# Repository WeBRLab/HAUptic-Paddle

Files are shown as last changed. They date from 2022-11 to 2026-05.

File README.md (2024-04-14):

# Haptic Paddle
<h2> This repository contains the design files and software for a single-DOF haptic display for STEM education.</h1>

<br/><br/><br/>
By: Auburn University Wearable and Bio-Robotics Lab <br/>
PI: **Chad G. Rose**  <br/>
Graduate Researchers: **Chandler Stubbs**, **Rhet Hailey**, **Avinash Baskaran**  <br/>
Undergraduate Researchers: **Zack Miller**, **Jamison Hood** <br/>

Instructions for flashing new code in Python:

1. Follow this tutorial to install micropython and configure micropython interpretter on logic board:
https://docs.sunfounder.com/projects/thales-kit/en/latest/micropython/python_start/install_micropython_to_pico.html

2. Run or Save your code on the RPI logic board as "main.py"

3. (optional) eject and re-insert USB cable to start code automatically.

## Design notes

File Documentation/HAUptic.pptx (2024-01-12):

## HAUptic Paddle

Avinash Baskaran
Chad G. Rose

## Hardware: Commercial Components

## Hardware: 3D Printing

## Electronics: PCB

## Electronics: PCB internal connections

GND
DNC
DNC
DNC
HIGH
Dir (1/0)
Dir (1/0)
PWM

….

GND
Motor (+)
Motor (-)
DNC
DNC
GND
Supply (5v) +
Supply (12v) +

…

DNC

## Electronics: PCB external connections

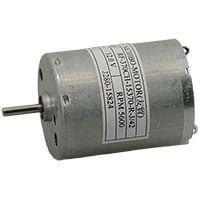
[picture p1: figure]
RF370CH-15370-R

DNC

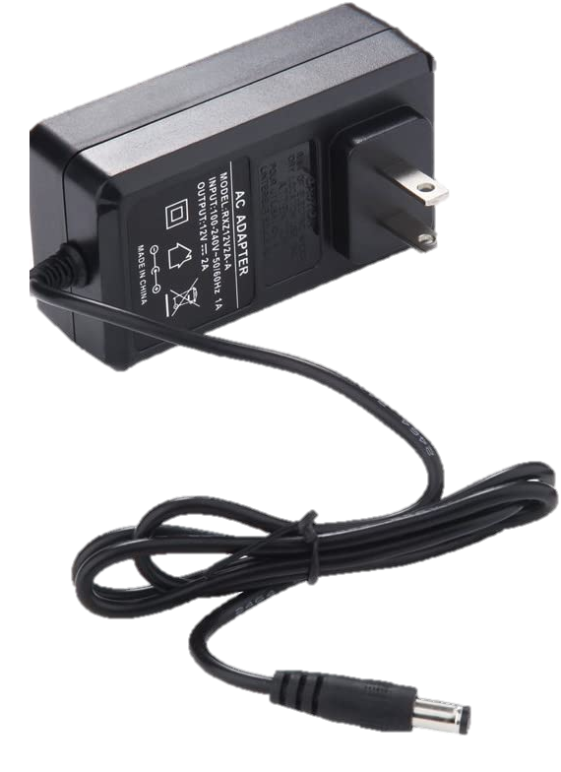
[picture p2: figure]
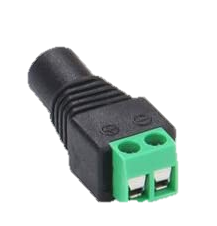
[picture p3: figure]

## Electronics: PCB external connections

DNC

## Software: Interfacing

## Assembly

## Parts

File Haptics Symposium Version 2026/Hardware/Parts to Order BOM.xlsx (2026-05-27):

Item | Cost Per Pack | No. Per Pack | No. Per Paddle | Cost Per Paddle | Vendor | Link | Column1
PLA (~.2 kg/paddle) | $28.00 | 1 | 0.2 | $5.60 | Amazon | https://www.amazon.com/HATCHBOX-Printer-Filament-Dimensional-Accuracy/dp/B09G8HDL1Q
Xiao Seeed ESP32S3 | $7.49 | 1 | 1 | $7.49 | Digikey | https://www.digikey.com/en/products/detail/seeed-technology-co-ltd/113991114/19285530?gclsrc=aw.ds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 | **Version Used for Evaluating Usability Between Low Cost and High End Haptic Paddles (Haptics Symposium 2026)
Xiao Boards (RP2040) | $6.50 | 1 | 1 | $6.50 | Mouser | https://www.mouser.com/ProductDetail/Seeed-Studio/102010388?qs=hd1VzrDQEGhCsl7tLa3o%252Bg%3D%3D&mgh=1 | **Version Used for Work-in-Progress Interface and Design Upgrades to Design Paper (Haptics Symposium 2026)
5V Voltage Regulator (Pololu 0J8557) | $8.95 | 1 | 1 | $8.95 | Pololu | Pololu 5V, 500mA Step-Down Voltage Regulator D24V5F5 (https://www.pololu.com/product/2843)
Motor Drivers | $14.50 | 1 | 1 | $14.50 | Sparkfun | https://www.sparkfun.com/sparkfun-motor-driver-dual-tb6612fng-with-headers.html
Cables | $15.00 | 33 | 1 | $0.45 | Amazon | https://www.amazon.com/Gauge-Wire-Solid-Hookup-Wires/dp/B088KQFHV7
Motors | $4.95 | 1 | 1 | $4.95 | Jameco | https://www.jameco.com/z/RF370CH-15370-R-Nichibo-Taiwan-12V-DC-Motor-5600-RPM-2mm-Round-Shaft_2327887.html
Bearings/bushings | $0.92 | 1 | 1 | $0.92 | McMaster | https://www.mcmaster.com/2938T3/
Shoulder bolt | $6.88 | 1 | 1 | $6.88 | McMaster | https://www.mcmaster.com/90311A144/
Neoprene Tubing | $1.27 | 1 | 0.08333333333 | $0.11 | McMaster | https://www.mcmaster.com/51075K27/
Solder | $7.39 | 50 | 5 | $0.74 | Amazon | https://www.amazon.com/TOWOT-Electrical-Soldering-Content-Sn60-Pd40/dp/B0943TPRXK
Heat shrink | $9.00 | 32.81 | 0.5 | $0.14 | Amazon | https://www.amazon.com/Othmro-Pieces-Heat-Shrinking-Ratio/dp/B07W4NZSSN
Magnets | $3.93 | 1 | 1 | $3.93 | McMaster | https://www.mcmaster.com/57295K73/
Sensor | $6.65 | 1 | 1 | $6.65 | Digikey | SS49E Honeywell Sensing and Productivity Solutions | Linear, Compass (ICs) | DigiKey (https://www.digikey.com.au/en/products/detail/honeywell-sensing-and-productivity-solutions/SS49E/701361)
Female header connector | $9.99 | 60 | 0.125 | $0.02 | Amazon | https://www.amazon.com/Qunqi-2-54mm-Straight-Connector-Arduino/dp/B07CGGSDWF
10-24 Steel Hex Nut | $2.33 | 100 | 1 | $0.02 | McMaster | https://www.mcmaster.com/90480A011/
8-32 Steel Hex Nut | $2.02 | 100 | 4 | $0.08 | McMaster | https://www.mcmaster.com/90480A009/
10-44 Steel Hex Nut | $2.33 | 100 | 1 | $0.02 | McMaster | https://www.mcmaster.com/90480A011/
PCB | Contact ___mdm0115@auburn.edu____ |  |  | $2.33
 |  |  | Price Per Paddle | $62.79 | Without WiFI
 |  |  |  | $63.78 | With WiFi
If Desired/Needed for Connection
Rubber Feet | $24.94 | 10 | 4 | $9.98 | McMaster | https://www.mcmaster.com/53535A22/ |  | Useful for a sturdy connection to test surface
Power supplies | $13.99 | 2 | 1 | $7.00 | Amazon | https://www.amazon.com/ALITOVE-Converter-100-240V-Transformer-Security/dp/B082C6XF88?hvadid=694095447987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 |  | Useful if desired to plug into a wall outlet
USB cable | $13.00 | 2 | 1 | $6.50 | Amazon | https://www.amazon.com/Upgrade-CONMDEX-Android-Charging-Transfer/dp/B087JMJSVC |  | Necessary if lacking a USB/USB-C Cable

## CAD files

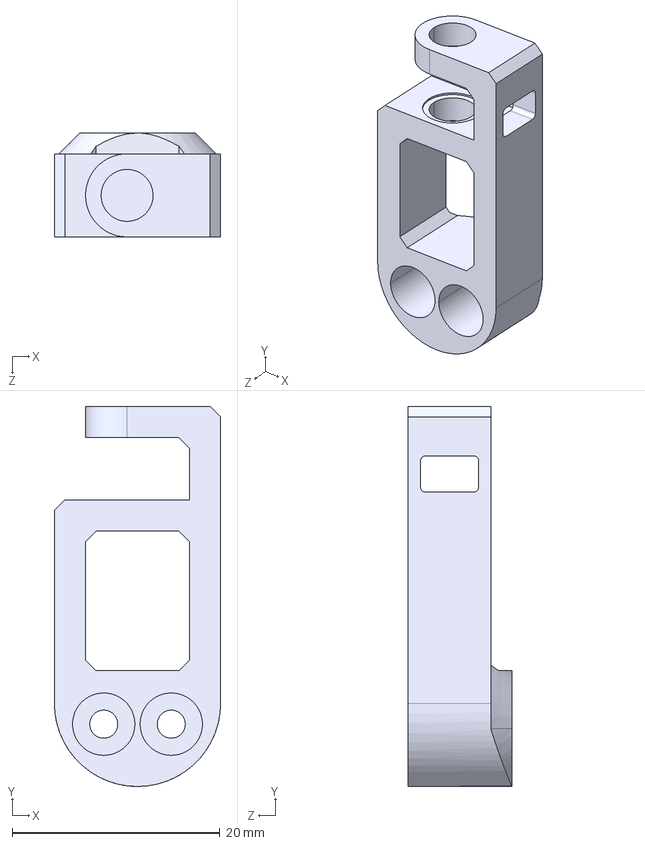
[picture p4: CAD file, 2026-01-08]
Haptics Symposium Version 2026/Hardware/STEP Files/Magnet Holder.STEP
16.0 x 36.6 x 10.0 mm

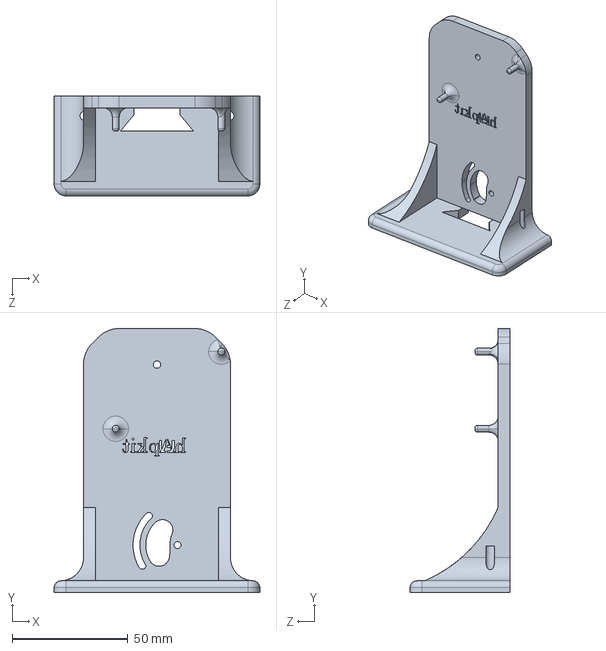
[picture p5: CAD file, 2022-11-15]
Hardware/step/Base_A-1.STEP
88.9 x 114.1 x 43.2 mm

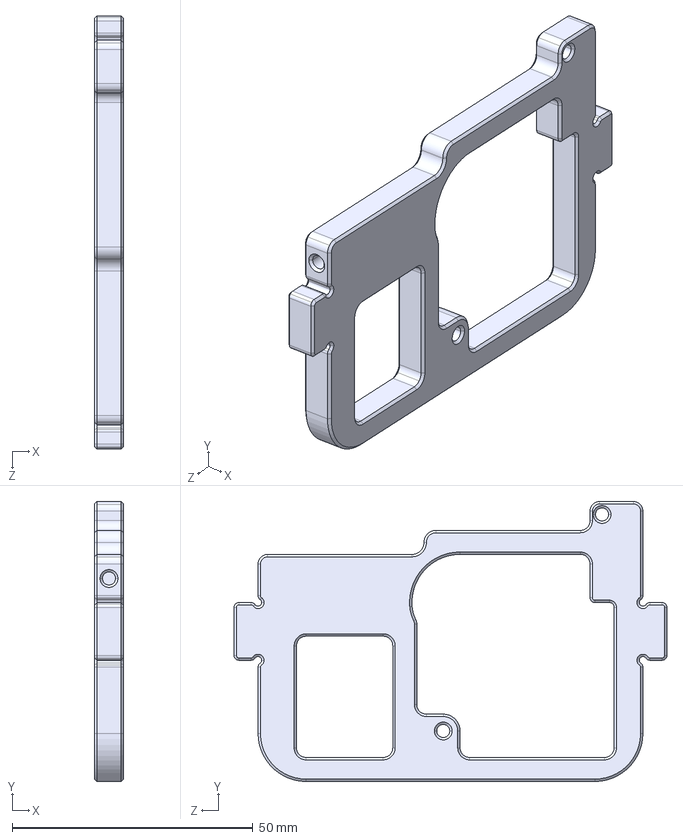
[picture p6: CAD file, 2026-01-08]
Haptics Symposium Version 2026/Hardware/STEP Files/Paddle - PCB Plate.STEP
6.00 x 58.2 x 90.0 mm

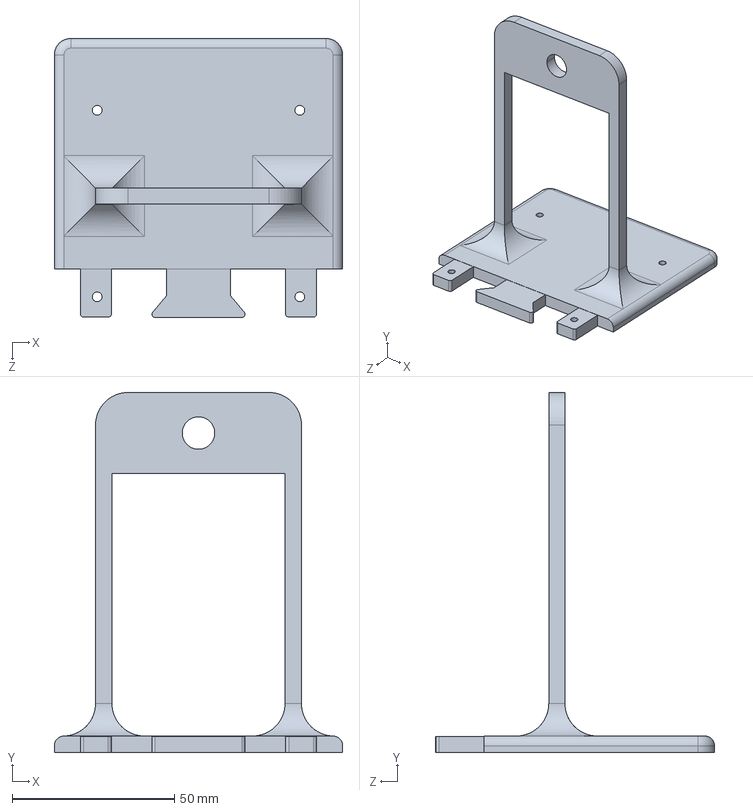
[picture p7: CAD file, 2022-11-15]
Hardware/step/Base_B-1.STEP
88.9 x 111.0 x 86.1 mm

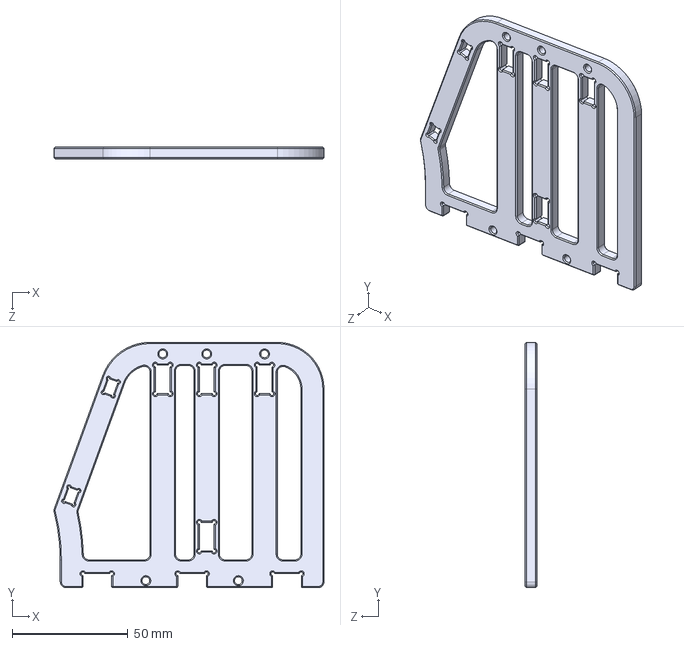
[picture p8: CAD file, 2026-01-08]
Haptics Symposium Version 2026/Hardware/STEP Files/Paddle - Side Plate.STEP
116.7 x 106.0 x 5.00 mm

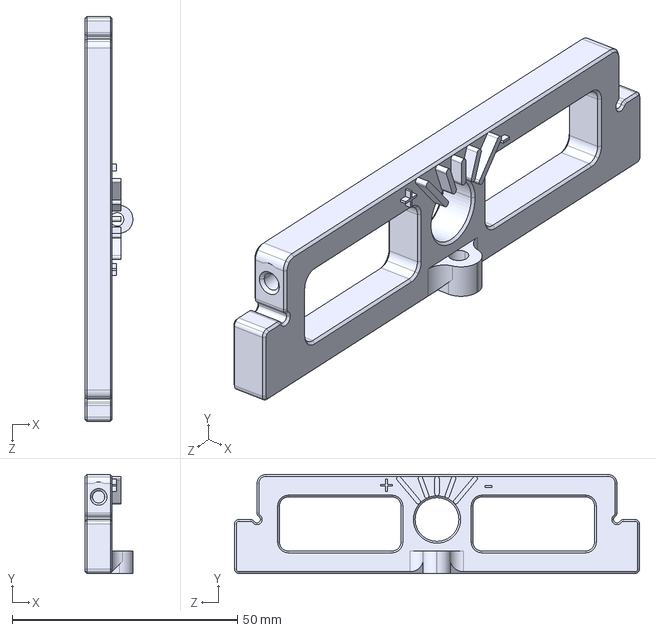
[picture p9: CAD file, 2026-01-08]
Haptics Symposium Version 2026/Hardware/STEP Files/Front Calibration Support Plate.STEP
10.6 x 22.0 x 90.0 mm

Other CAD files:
Haptics Symposium Version 2026/Hardware/Solidworks Files/Assembly/HapKit Assembly.SLDASM
Hardware/HAUPTIC_PADDLE.SLDASM
Hardware/CAD/tb6612fng.step.SLDASM
Hardware/CAD/Assembly.SLDASM
Hardware/CAD/capacitor.step.SLDPRT
Hardware/CAD_files/Sector_Pulley - adjusted.SLDPRT
Hardware/Base_B.SLDPRT
Hardware/CAD/Motor_Paddle_Interface.step.SLDPRT
Hardware/CAD_files/Base.1.SLDPRT
Hardware/Base_A.SLDPRT
Hardware/CAD/header_8.step.SLDPRT
Hardware/CAD_files/Sector_Pulley_1.SLDPRT
Haptics Symposium Version 2026/Hardware/STEP Files/Mini Plate with Nut.STEP
Haptics Symposium Version 2026/Hardware/STEP Files/Motor_Pulley.STEP
Haptics Symposium Version 2026/Hardware/STEP Files/Paddle - Bottom Plate.STEP
Haptics Symposium Version 2026/Hardware/STEP Files/Paddle - PCB Side Plate.STEP
Haptics Symposium Version 2026/Hardware/STEP Files/Paddle - Washer.STEP
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

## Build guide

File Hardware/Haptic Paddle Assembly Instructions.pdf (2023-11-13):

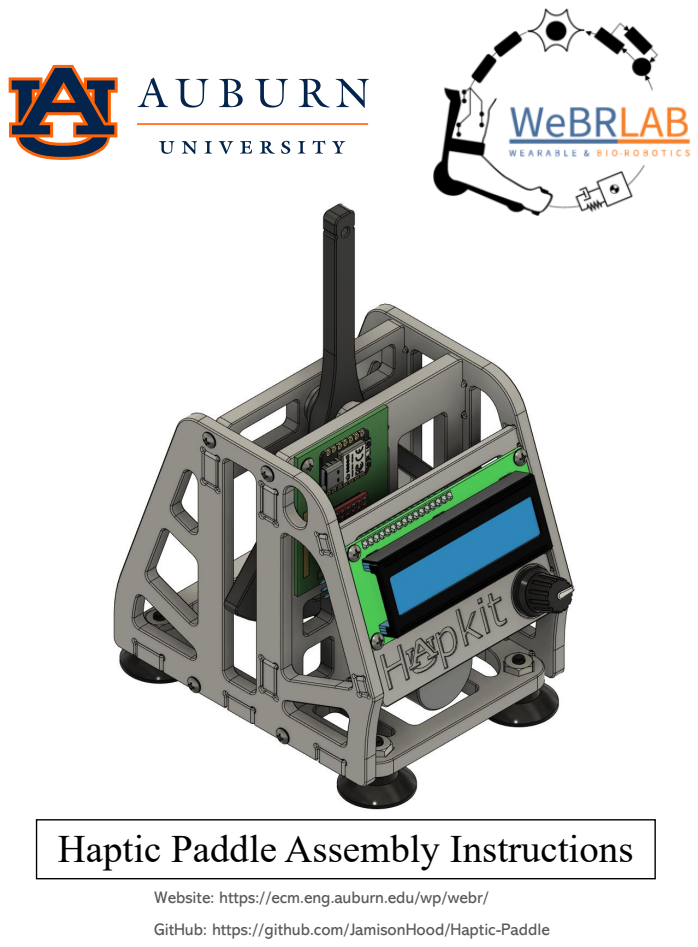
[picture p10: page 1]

Haptic Paddle Assembly Instructions

Website: https://ecm.eng.auburn.edu/wp/webr/

GitHub: https://github.com/JamisonHood/Haptic-Paddle

P a g e | 2

## Table of Contents

## Required Components

## Electronics

Part Name | Quantity | Image
Rotary Encoder | 1

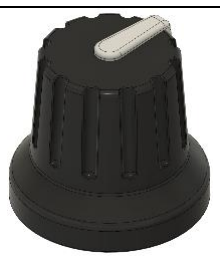
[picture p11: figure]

Encoder Knob | 1
Control Board | 1
Brushed Motor | 1

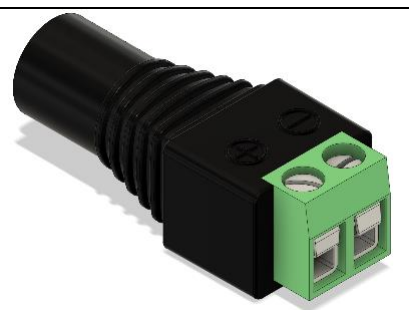
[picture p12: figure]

Barrel Power Connector | 1

LCD Display | 1

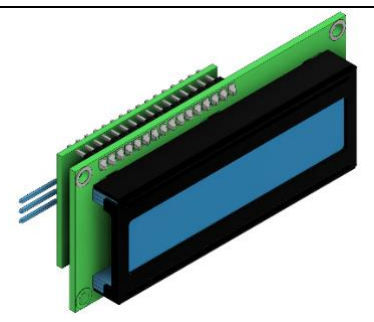
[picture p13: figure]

## Hardware

Part Name | Quantity | Image
¼ Inch Shoulder Bolt | 1
¼ Inch Sleeve Bushing | 1

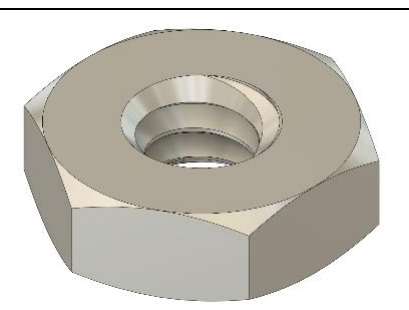
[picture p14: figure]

10-24 Nut (For Shoulder Bolt) | 1
Rubber Feet | 4

8-32 Nut (For Rubber Feet) | 4

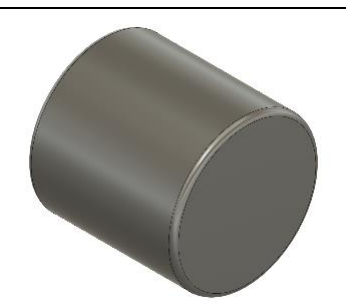
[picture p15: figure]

Disc Magnet | 1

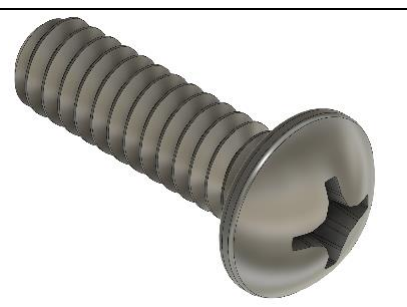
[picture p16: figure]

18-8 Pan Head Screw | 16

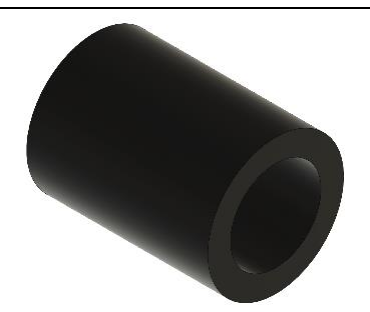
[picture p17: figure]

Rubber Sleeve | 1

## 3D printed Components

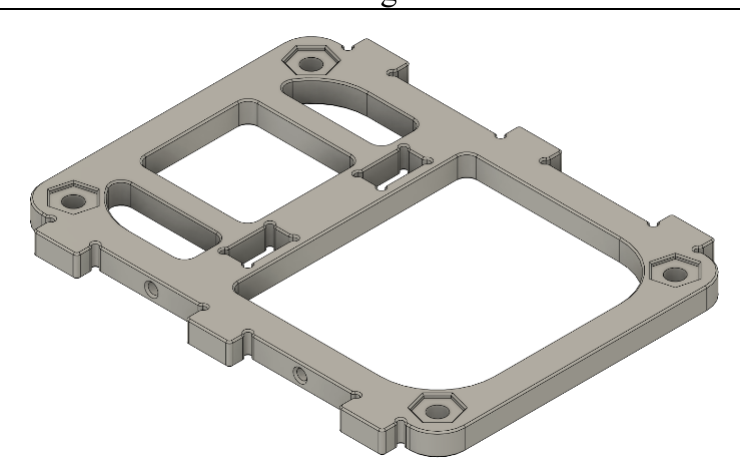
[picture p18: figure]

Part Name | Quantity | Image
Base Plate | 1
Motor and Electronics Plate | 1
LCD Frame | 1

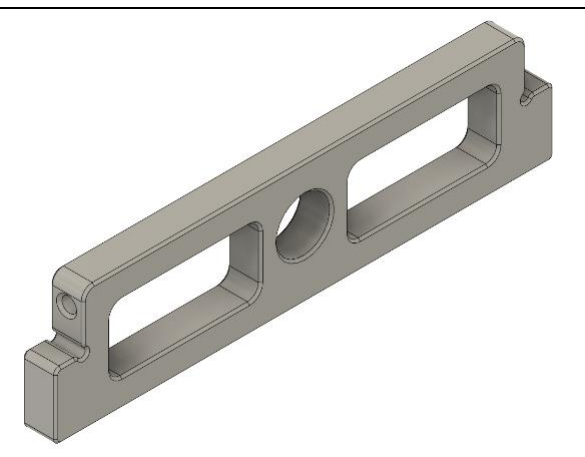
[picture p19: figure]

Shoulder Support Plate | 1

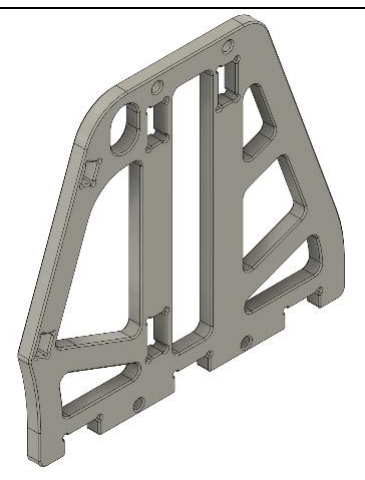
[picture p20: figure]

Left Side Plate | 1
Right Side Plate | 1

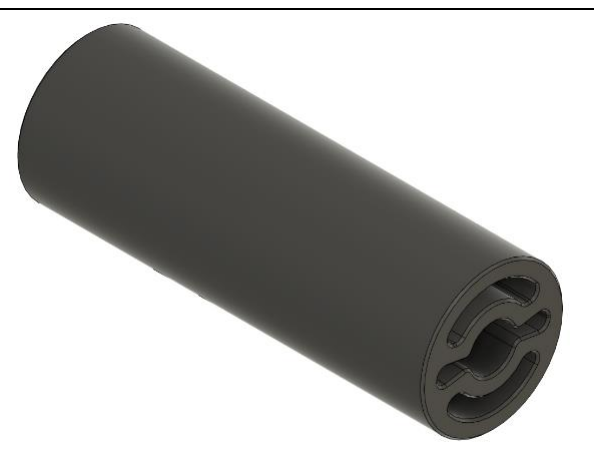
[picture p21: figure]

Motor Pulley | 1

P a g e |

8

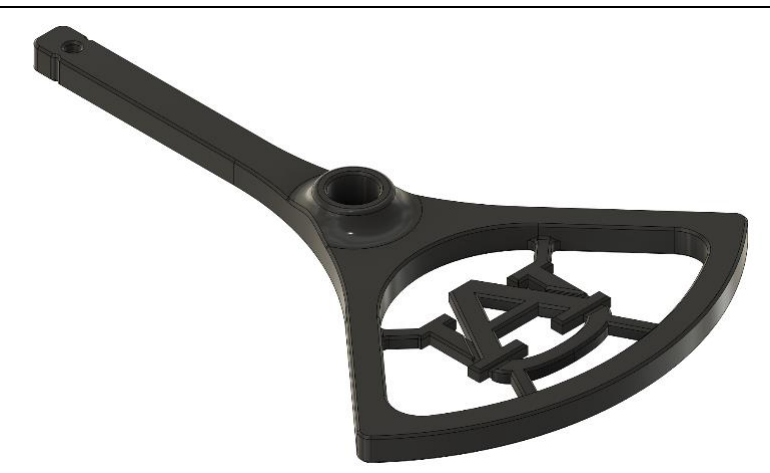
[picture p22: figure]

Paddle
1

1 | Assembly Steps

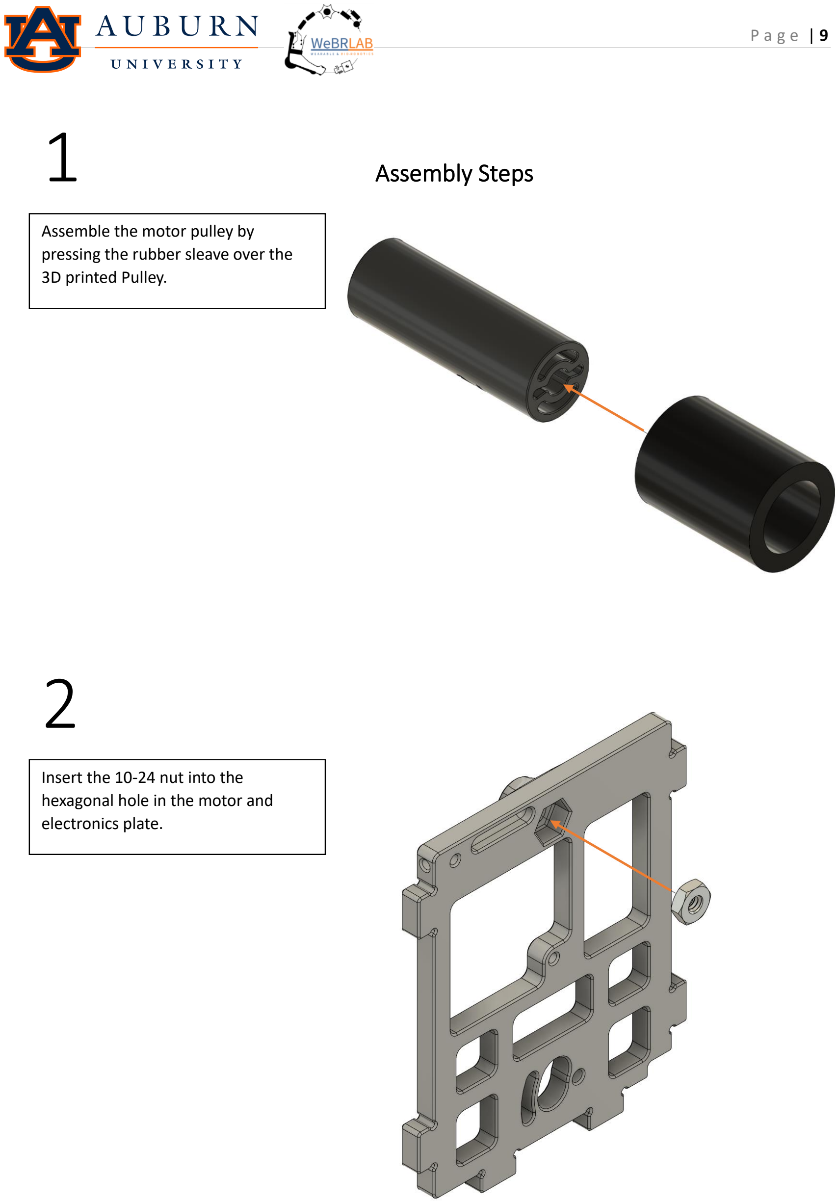
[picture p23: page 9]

2

Assemble the motor pulley by pressing the rubber sleave over the 3D printed Pulley.

Insert the 10-24 nut into the hexagonal hole in the motor and electronics plate.

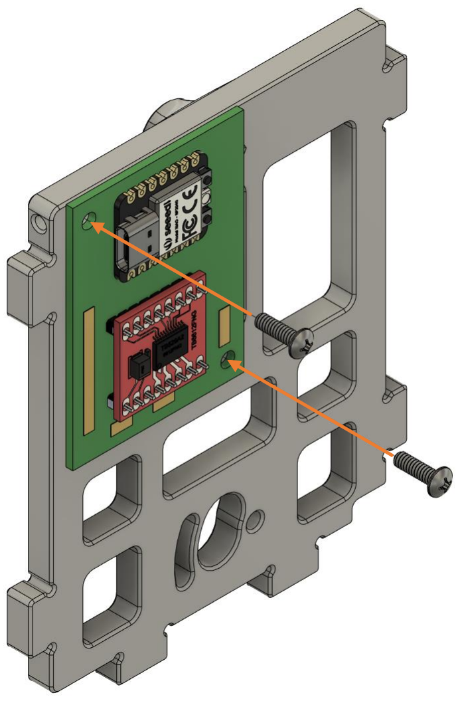
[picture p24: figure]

3

4

Attach the electronics PCB using 2 #18-8 Screws.

Note: Make sure the #10-24 nut is in place as it will not be accessible after this step.

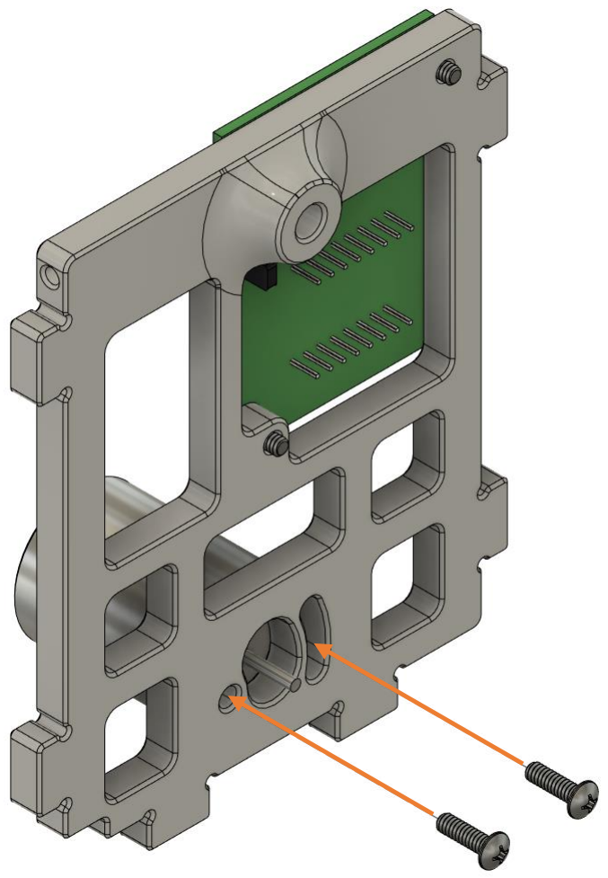
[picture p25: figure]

Attach the brushed motor using 2 #18-8 screws. Leave the screws loose such that the motor can freely swing in its mount.

5

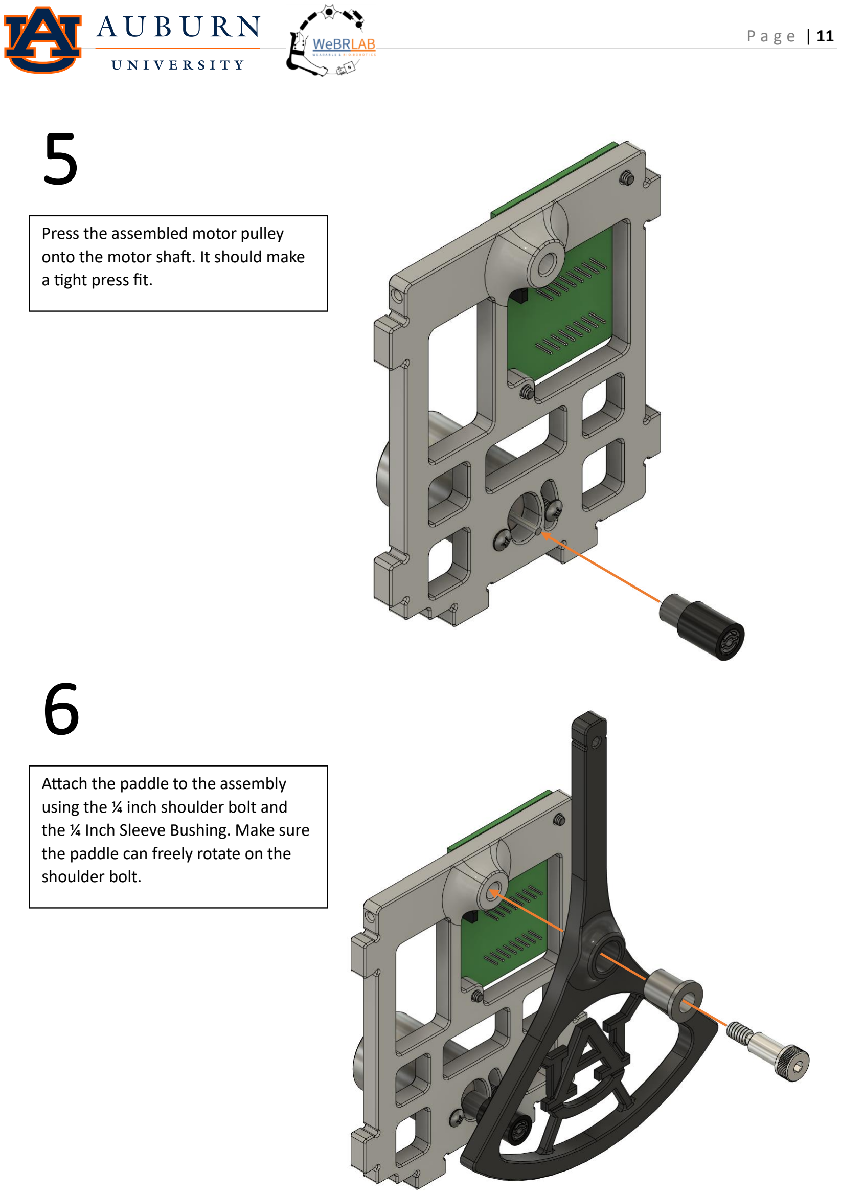
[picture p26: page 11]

6

Press the assembled motor pulley onto the motor shaft. It should make a tight press fit.

Attach the paddle to the assembly using the ¼ inch shoulder bolt and the ¼ Inch Sleeve Bushing. Make sure the paddle can freely rotate on the shoulder bolt.

7

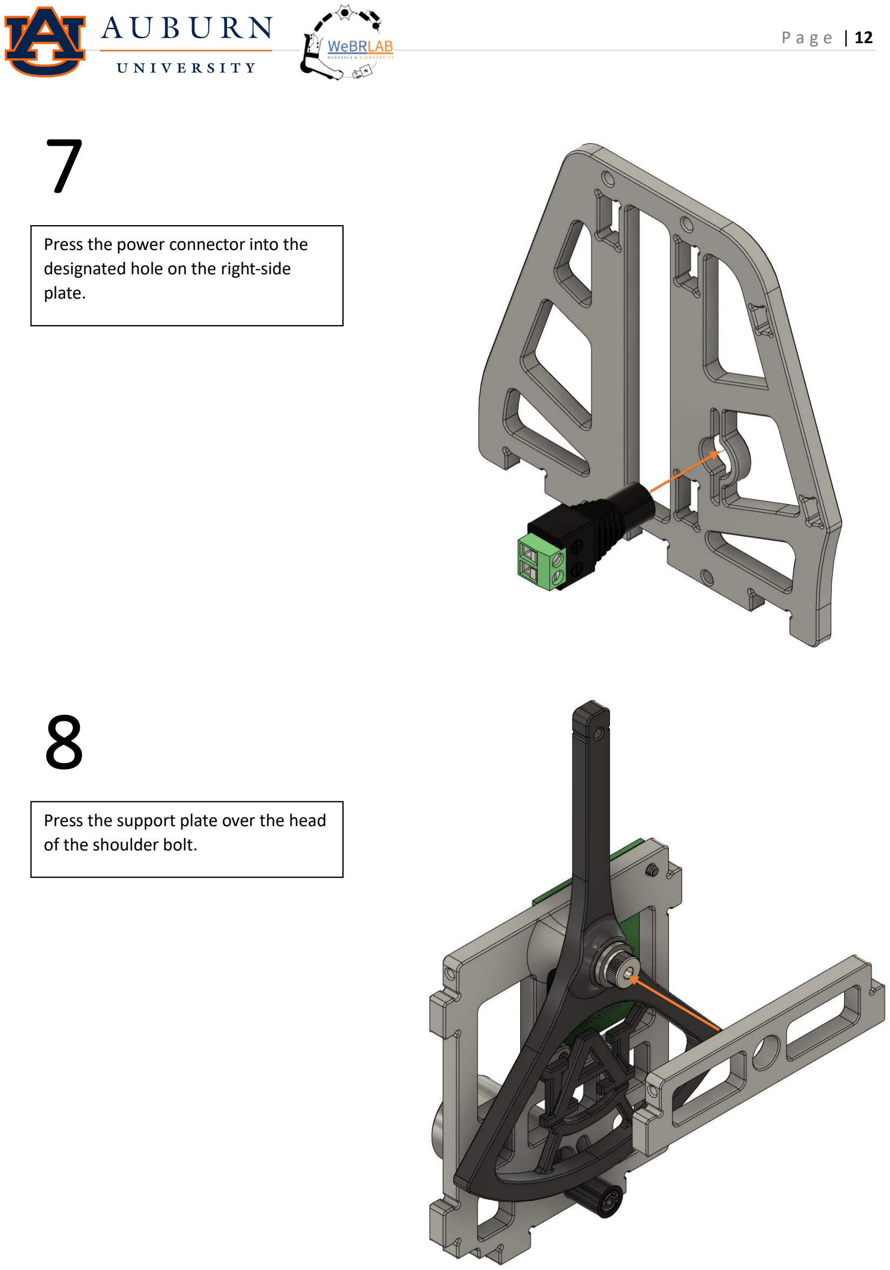
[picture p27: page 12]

8

Press the power connector into the designated hole on the right-side plate.

Press the support plate over the head of the shoulder bolt.

9

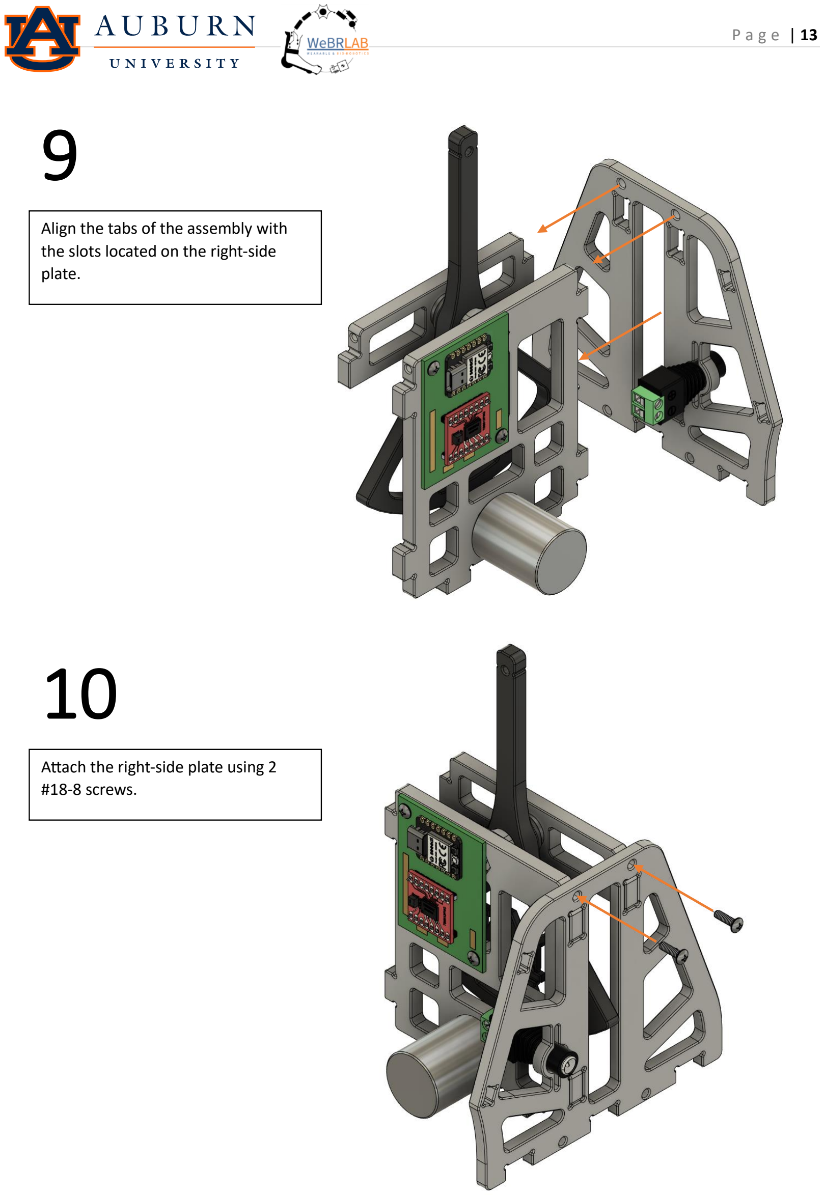
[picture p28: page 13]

10

Align the tabs of the assembly with the slots located on the right-side plate.

Attach the right-side plate using 2 #18-8 screws.

11

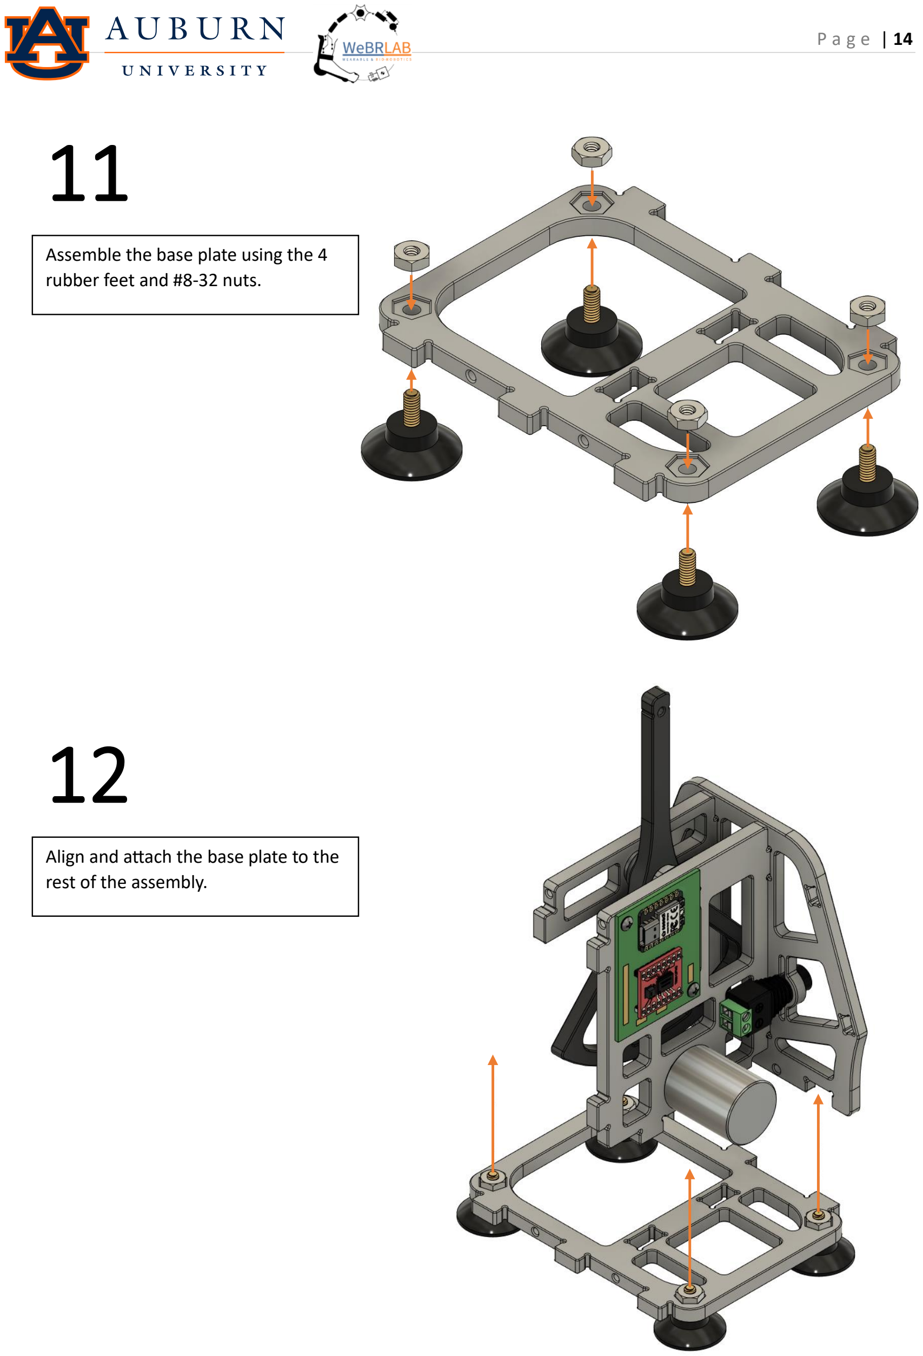
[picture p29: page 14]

12

Assemble the base plate using the 4 rubber feet and #8-32 nuts.

Align and attach the base plate to the rest of the assembly.

13

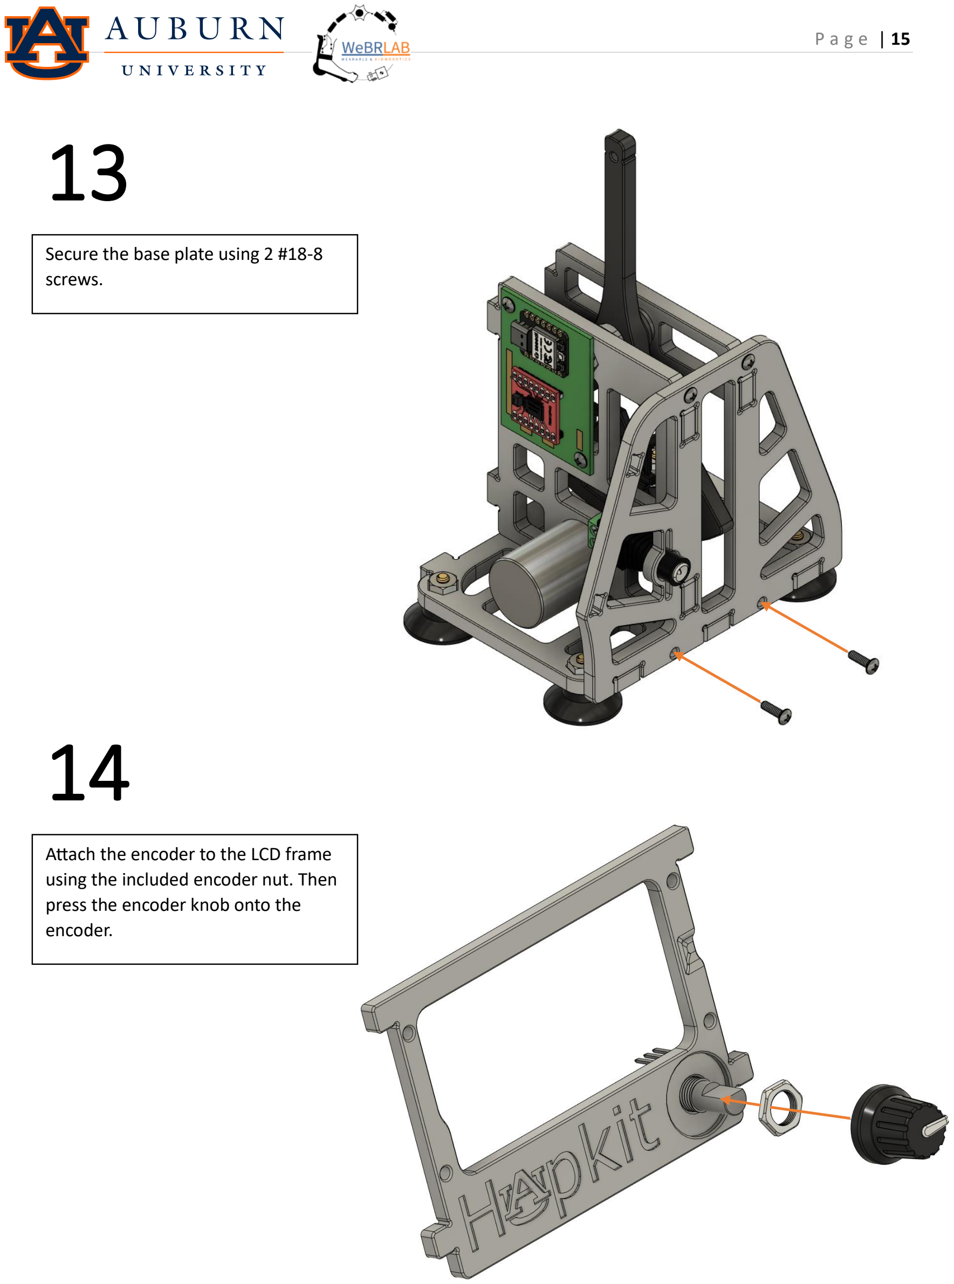
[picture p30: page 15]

14

Secure the base plate using 2 #18-8 screws.

Attach the encoder to the LCD frame using the included encoder nut. Then press the encoder knob onto the encoder.

15

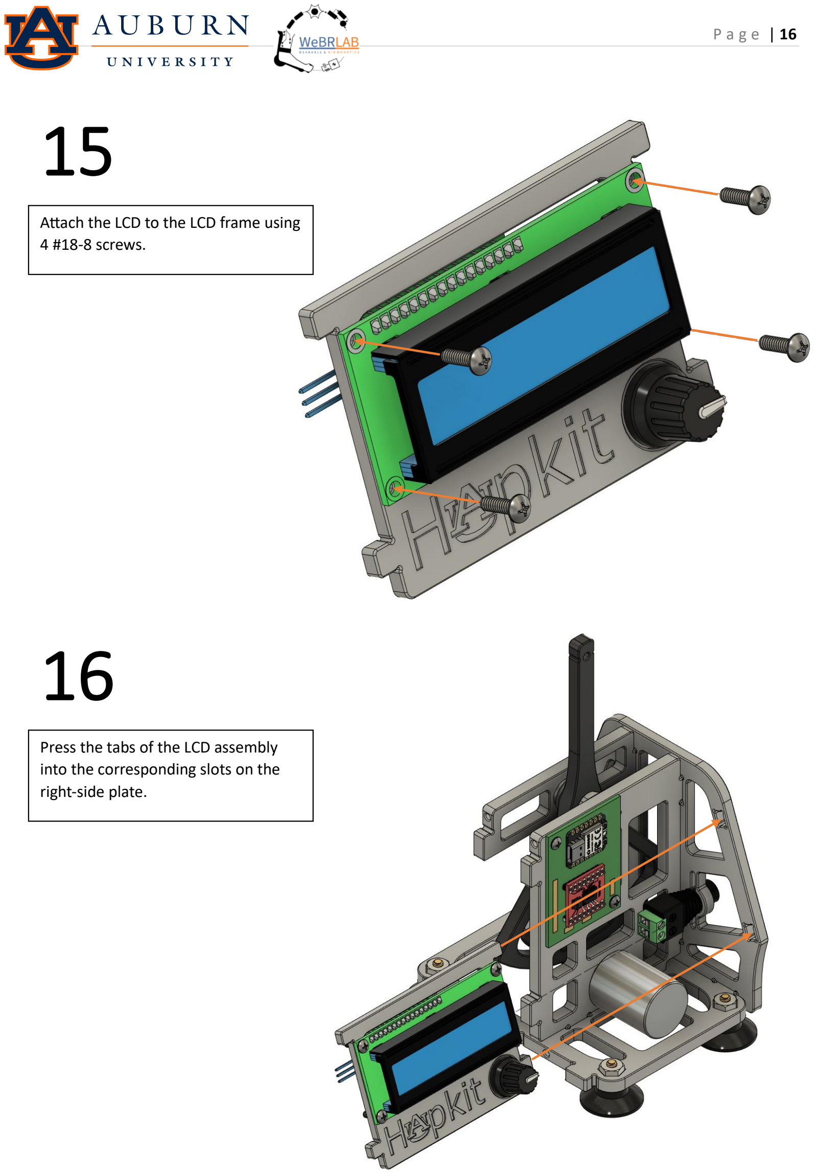
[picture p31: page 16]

16

Attach the LCD to the LCD frame using 4 #18-8 screws.

Press the tabs of the LCD assembly into the corresponding slots on the right-side plate.

17

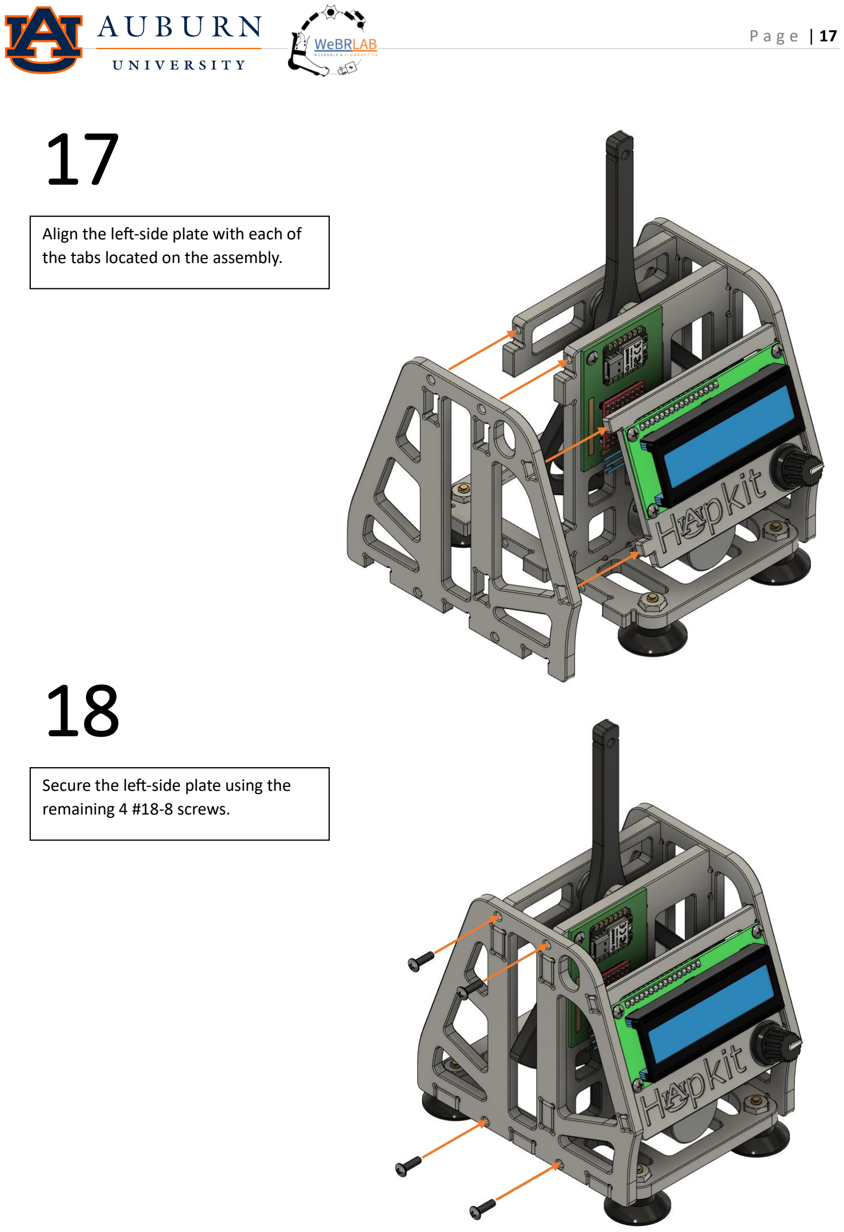
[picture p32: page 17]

18

Align the left-side plate with each of the tabs located on the assembly.

Secure the left-side plate using the remaining 4 #18-8 screws.

19

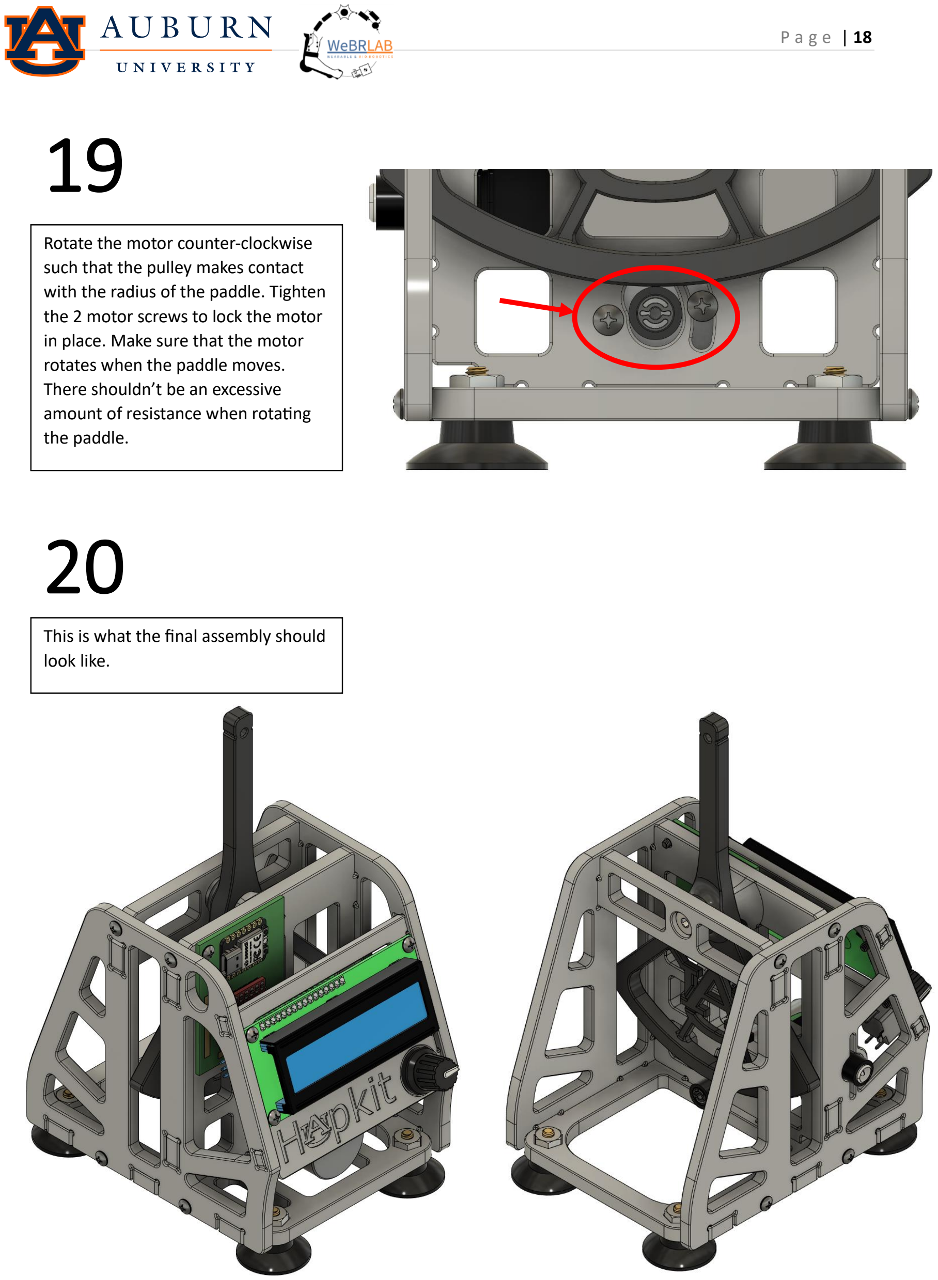
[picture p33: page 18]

Rotate the motor counter

-clockwise
such that the pulley makes contact with the radius of the paddle. Tighten the 2 motor screws to lock the motor in place. Make sure that the motor rotates when the paddle moves. There shouldn’t be an excessive amount of resistance when rotating the paddle.
20

This is what the final assembly should look like.

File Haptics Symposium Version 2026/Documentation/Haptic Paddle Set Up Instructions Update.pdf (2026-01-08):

Set Up
1. Replace the front support piece with the calibration support bar, pictured below. Mark a centerline in the paddle arm for calibration.

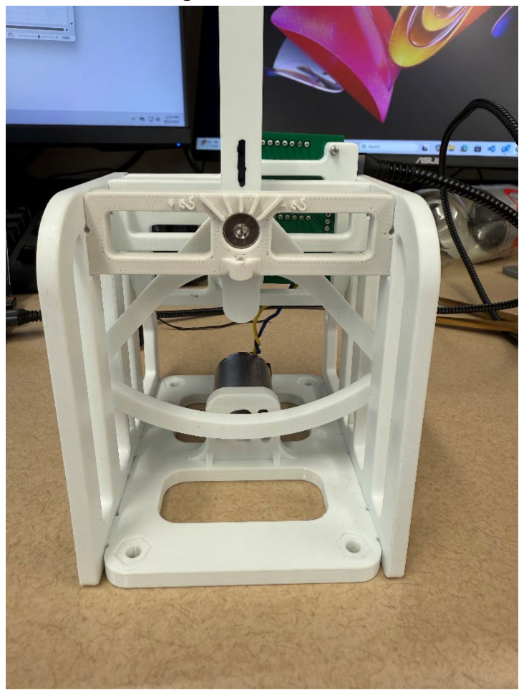
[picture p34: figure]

2. Ensure the shoulder bolt is tightened enough to reduce perpendicular shifting of the paddle. It will feel relatively tight.

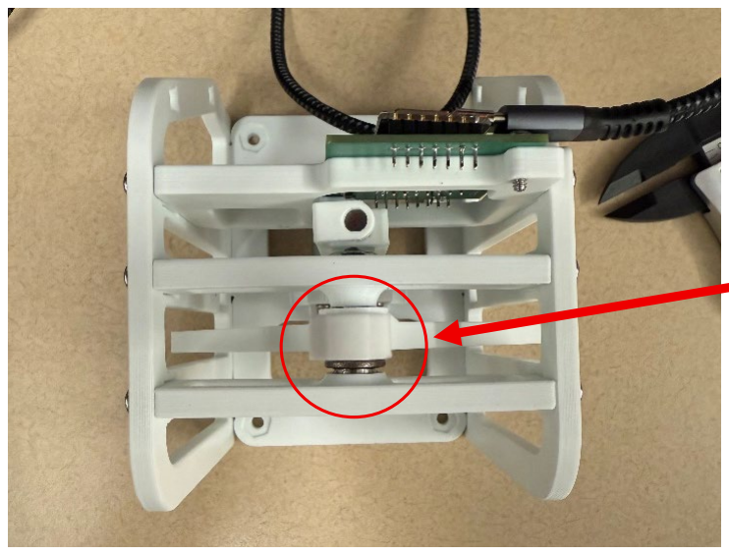
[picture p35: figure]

Should be very little shift front to back

0

+ -

Connecting to the Xiao RP2040 using the Arduino IDE https://wiki.seeedstudio.com/XIAO-RP2040-with-Arduino/
Calibration
1. Using the calibration support bar and the attached Calibration sketch, record sensor values for each angle position (+40, +20, 0, -20, -40 using the reference frame defined above) using the serial monitor in the Arduino IDE. Sensor readings should ideally be

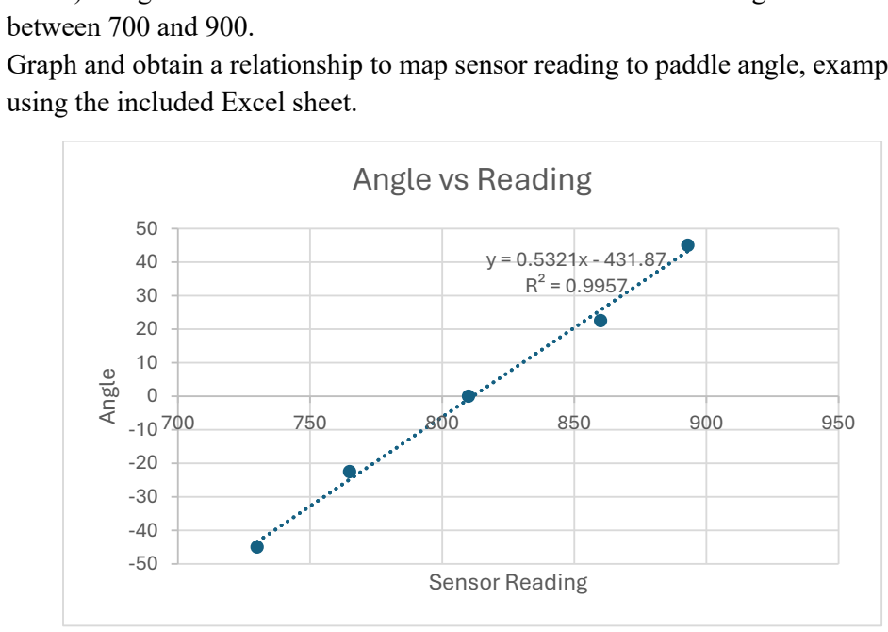
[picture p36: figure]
between 700 and 900.; using the included Excel sheet.; Angle; Sensor Reading; Angle vs Reading

2. Graph and obtain a relationship to map sensor reading to paddle angle, exampled below,
3. Integrate this new relationship into the DesiredPosition sketch to finish calibrating the device.

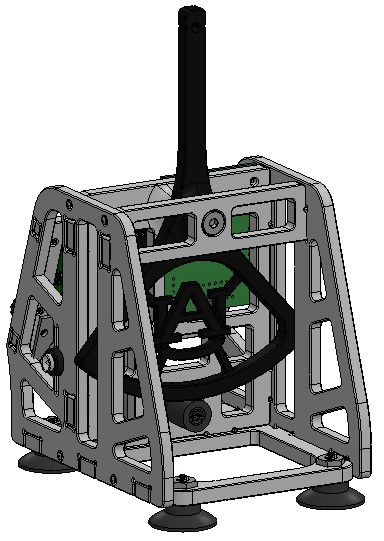
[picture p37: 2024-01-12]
Hardware/CAD/Assembly.JPG

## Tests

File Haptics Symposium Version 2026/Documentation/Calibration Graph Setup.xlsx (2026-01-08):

Sensor Reading | Angle

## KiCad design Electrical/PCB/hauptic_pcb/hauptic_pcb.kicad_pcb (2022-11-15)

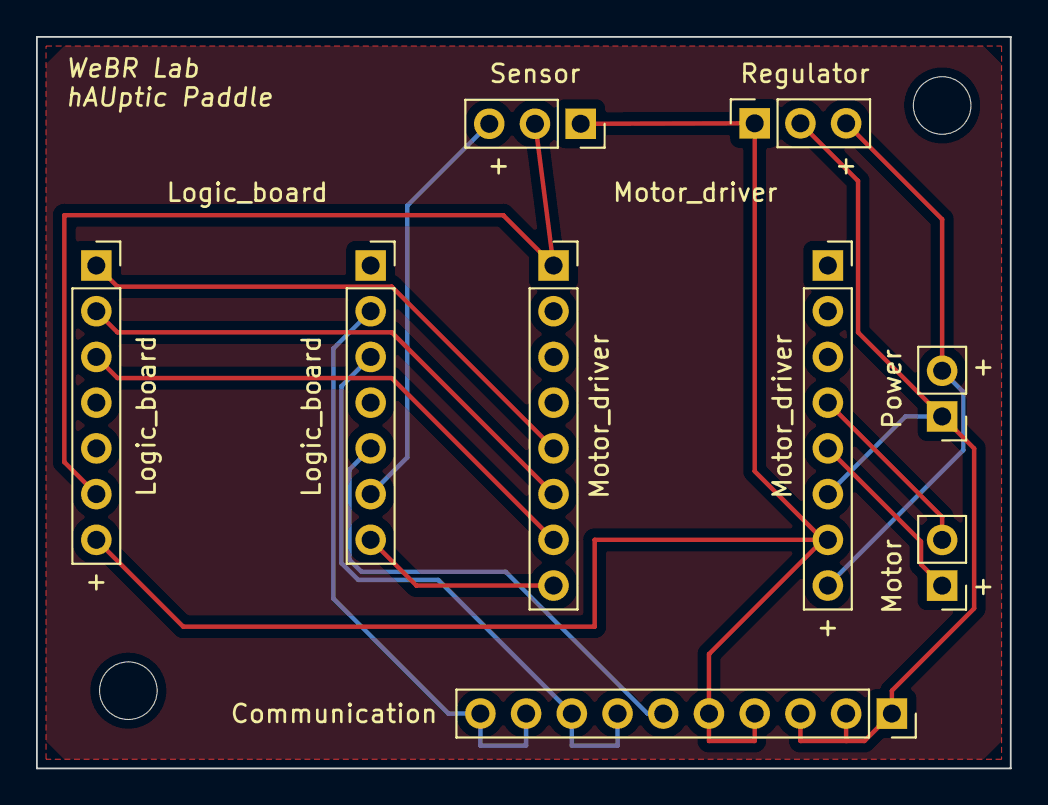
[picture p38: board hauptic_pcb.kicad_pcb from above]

Board: 2 copper layers, 54.1 x 40.6 mm, 9 parts (0 on the bottom side), 14 nets.

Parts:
Communication: Conn_01x10_Female; PinSocket_1x10_P2.54mm_Vertical
Logic_board: Conn_01x07_Female; PinSocket_1x07_P2.54mm_Vertical
Logic_board#2: Conn_01x07_Female; PinSocket_1x07_P2.54mm_Vertical
Motor: Conn_01x02_Male; PinHeader_1x02_P2.54mm_Vertical
Motor_driver: Conn_01x08_Female; PinSocket_1x08_P2.54mm_Vertical
Motor_driver#2: Conn_01x08_Female; PinSocket_1x08_P2.54mm_Vertical
Power: Conn_01x02_Male; PinHeader_1x02_P2.54mm_Vertical
Regulator: Conn_01x03_Female; PinSocket_1x03_P2.54mm_Vertical
Sensor: Conn_01x03_Female; PinSocket_1x03_P2.54mm_Vertical

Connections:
unnamed: Communication.1, Communication.2, Communication.3, Motor_driver.6, Power.1, Regulator.2
unnamed: Communication.4, Communication.5, Logic_board#2.7, Motor_driver.7, Regulator.1, Sensor.1
unnamed: Communication.6, Logic_board.5
unnamed: Communication.7, Communication.8, Logic_board.3
unnamed: Communication.9, Communication.10, Logic_board.2
unnamed: Logic_board#2.1, Motor_driver#2.5
unnamed: Logic_board#2.2, Motor_driver#2.6
unnamed: Logic_board#2.3, Motor_driver#2.7
unnamed: Logic_board.7, Motor_driver#2.8
unnamed: Motor_driver.8, Power.2, Regulator.3
unnamed: Motor.2, Motor_driver.4
unnamed: Motor.1, Motor_driver.5
unnamed: Logic_board#2.6, Motor_driver#2.1, Sensor.2
unnamed: Logic_board.6, Sensor.3

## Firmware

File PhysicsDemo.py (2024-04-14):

from machine import Pin, I2C
from pico_i2c_lcd import I2cLcd
import utime
import math

# Global variables
stdby_pin = machine.Pin(1, machine.Pin.OUT)
a1_pin = machine.Pin(2, machine.Pin.OUT)
a2_pin = machine.Pin(4, machine.Pin.OUT)
pwma_pin = machine.Pin(26)

# Functions to initialize sensor and driver
def init_sensor():
    adc_pin = machine.ADC(machine.Pin(27))
    return adc_pin

def init_driver():
    pwm = machine.PWM(pwma_pin)
    pwm.freq(1000)  # Set PWM frequency
    stdby_pin.value(1)  # Set standby pin to high
    return pwm

# Function to drive motor
def drive(speed, pwm):
    if speed <= 0:
        a1_pin.value(0)
        a2_pin.value(1)
    else:
        a1_pin.value(1)
        a2_pin.value(0)
    speed = abs(speed)
    pwm.duty_u16(round(speed))  # Corrected line

# Controller function
def control(kp, desired_position, position):
    maxspeed = 5000.0
    position_error = position - desired_position
    control_signal = kp * position_error
    if control_signal > maxspeed:
        control_signal = maxspeed
    if control_signal < -maxspeed:
        control_signal = -maxspeed
    return round(control_signal)

def init_encoder():
    pin_clk = Pin(6, Pin.IN, Pin.PULL_DOWN)
    pin_dt = Pin(7, Pin.IN, Pin.PULL_DOWN)
    return pin_clk, pin_dt

pin_clk, pin_dt = init_encoder()
clk_last = pin_clk.value()
counter = 0


def printThis(text):
    printSuccessful = 0
    I2C_ADDR = 0x27
    I2C_NUM_ROWS = 2
    I2C_NUM_COLS = 16
    while (printSuccessful == 0):
        i2c = I2C(1, sda=Pin(6), scl=Pin(7), freq=400000)
        try:
            lcd = I2cLcd(i2c, I2C_ADDR, I2C_NUM_ROWS, I2C_NUM_COLS)
            lcd.clear()
            lcd.putstr(text)
            printSuccessful = 1
            utime.sleep(.1)
        except:
            print("Error: please wait")
            
printThis("hAUptic Paddle: Physics Demo")


def getTheta(pos):
    # Convert position to angle (theta)
    angle = pos-484000 #* (2 * math.pi / 65535)  # Adjust scale and offset if needed
    angle = angle/20000*30+20
    return angle

wall_loc = 20

m = 10
g = 9.81  # Acceleration due to gravity (m/s^2)
L = 1.0   # Length of the pendulum (m)
dt = 0.1 # Time step for numerical integration

Kspring = [
    0.00,
    1.00,   
    0.00,
    1.00
]

Kdamp = [
    0.00,
    0.00,
    1.00,
    1.00
]


mode = 0
debounce = 0
iteration_count = 0
last_change_time = utime.ticks_ms()
adc = init_sensor()
pwm = init_driver()
pos = [0.0]
prev_pos = [0]
vel = [0]
itr = 0

kp = 7
kd = 20
ui_dt = 0
des_pos = 0
control_signal = 1;
while True:
    ui_dt += 0.01*itr
    ui_dt = ui_dt % .5
    clk_state = pin_clk.value()
    dt_state = pin_dt.value()
    if (ui_dt>= 0.1):
        if (clk_state != clk_last ):
            if dt_state != clk_state:
                mode -= 1
            else:
                mode += 1
            mode = mode % len(Kspring)
            printThis("Spring/Damper: \n"+ str(Kspring[mode]) + "/"+ str(Kdamp[mode]))
        clk_last = pin_clk.value()
        dt_last = dt_state
    prev_pos.append(pos[itr])
    utime.sleep(.01)
    p1 = 10*adc.read_u16()
    utime.sleep(.01)
    p2 = 10*adc.read_u16()
    utime.sleep(.01)
    p3 = 10*adc.read_u16()
    utime.sleep(.01)
    p = (getTheta(p1)+getTheta(p2)+getTheta(p3))/3
    if p>= 2:
        p += (p*p/10)
    pos.append(p)
    vel.append((getTheta(p3)-getTheta(p1))/.1)
    
    vel[itr] = sum(vel[-3:])/3
    pos_err = 0
    
    control_signal =  -pos[itr]*300
    if control_signal >= 0:
        control_signal = control_signal*5.5
    control_signal = control_signal/3.5*Kspring[mode]*1.25 - vel[itr]*Kdamp[mode]*250
    drive(control_signal, pwm)
    utime.sleep_ms(1)
    itr = itr +1
    print(control_signal)
    if itr>= 100:
        pos = [pos[itr]]
        vel = [vel[itr]]
        prev_pos = [prev_pos[itr]]
        itr = 0
        

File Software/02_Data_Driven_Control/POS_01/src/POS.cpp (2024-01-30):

#include <stdio.h>
#include "pico/stdlib.h"
#include "hardware/pwm.h"
#include "hardware/adc.h"
#include <math.h>

// GLOBAL VARIABLES:
const uint stdby = 1;
const uint a1 = 2;
const uint a2 = 4;
const uint pwma = 26;
const uint PIN = 5;

// FUNCIONS CALLED TO INITIALIZE SENSOR AND DRIVER //
void init_sensor(){
    adc_init();
    adc_gpio_init(27);
    adc_select_input(1);
    gpio_init(PIN);
    gpio_set_dir(PIN, GPIO_OUT);
    uint16_t position = 0;
}

void init_driver(){
    gpio_init(stdby);
    gpio_set_dir(stdby,GPIO_OUT);
    gpio_put(stdby,true);
    gpio_init(a1);
    gpio_set_dir(a1,GPIO_OUT);
    gpio_init(a2);
    gpio_set_dir(a2,GPIO_OUT);
    gpio_set_function(pwma,GPIO_FUNC_PWM);
    int slice_= pwm_gpio_to_slice_num(pwma); 
    int channel_= pwm_gpio_to_channel(pwma);
    pwm_set_enabled(slice_, true); 
    pwm_set_wrap(slice_, 12500);
    pwm_set_phase_correct(slice_, false);
 }

int getVelocity(int current_position, int last_position, int dt){
    float velocity = 10*(current_position - last_position)/(dt/1000);
    return velocity;
}

// FUNCION CALLED TO DRIVE MOTOR //
void drive(int speed){
    if(speed <= 0) {
        gpio_put(a1,false);
        gpio_put(a2,true);
    }
    else {
        gpio_put(a1,true);
        gpio_put(a2,false);
    }
    speed = abs(speed);
    pwm_set_gpio_level(pwma,speed);
    sleep_ms(1);
}

//  CONTROLLER //
float control(float kp, int desired_position, int position){
    float maxspeed = 5000.0;
    uint32_t amplification_factor = 1;          //      [degree/Volt]
    uint32_t paddleRadius = 1;                  //      [m]
    float position_error = position - desired_position;
    float control_signal = kp*(position_error);
    if (control_signal > maxspeed){
        control_signal = maxspeed;
    }
    if (control_signal < -1*maxspeed){
        control_signal = -1*maxspeed;
    }
    // control_signal = 0.0;
    int control_output = round(control_signal);
    return control_output;
}


// MAIN LOOP //
int main() {
    //  INITIALIZE PADDLE
    init_sensor();                          //      "turn on" sensor
    init_driver();                          //      "turn on" driver
    stdio_init_all();                       //      "turn on" logic board
    
   //  Declare CONSTANTS
    int current_position = 0;
    int last_position;
    int last_last_position;
    int current_velocity;
    int s_t;
    int e_t;
    int dt = 0.01;
    int T_ = 0;
    int count = 0;
    int control_signal;

    //  START CONTROL LOOP
    while (1){
        count = count +1;
        while (true) {
            s_t = time_us_32();
            last_last_position = last_position;
            last_position = current_position;
            sleep_ms(2);
            current_position = adc_read();
            e_t = time_us_32();
            dt = e_t - s_t;
            T_ = T_ + dt;
            current_velocity = getVelocity(current_position, last_position,dt);
            printf("%.2f ...", (float)current_velocity);
            printf("%.2f ...", (float)current_position);
            int current_position = adc_read();
            printf("%.2f \n", (float)T_);    
        }
    }
}

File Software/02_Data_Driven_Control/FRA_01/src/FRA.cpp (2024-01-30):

#include <stdio.h>
#include "pico/stdlib.h"
#include "hardware/pwm.h"
#include "hardware/adc.h"
#include <math.h>
#include <hardware/timer.h>

// GLOBAL VARIABLES:
const uint stdby = 1;
const uint a1 = 2;
const uint a2 = 4;
const uint pwma = 26;
const uint PIN = 5;

// FUNCIONS CALLED TO INITIALIZE SENSOR AND DRIVER //
void init_sensor(){
    adc_init();
    adc_gpio_init(27);
    adc_select_input(1);
    gpio_init(PIN);
    gpio_set_dir(PIN, GPIO_OUT);
    uint16_t position = 0;
}
void init_driver(){
    gpio_init(stdby);
    gpio_set_dir(stdby,GPIO_OUT);
    gpio_put(stdby,true);
    gpio_init(a1);
    gpio_set_dir(a1,GPIO_OUT);
    gpio_init(a2);
    gpio_set_dir(a2,GPIO_OUT);
    gpio_set_function(pwma,GPIO_FUNC_PWM);
    int slice_= pwm_gpio_to_slice_num(pwma); 
    int channel_= pwm_gpio_to_channel(pwma);
    pwm_set_enabled(slice_, true); 
    pwm_set_wrap(slice_, 12500);
    pwm_set_phase_correct(slice_, false);
 }
int getVelocity(int current_position, int last_position, int dt){
    float velocity = 10*(current_position - last_position)/(dt/1000);
    return velocity;
}

// FUNCION CALLED TO DRIVE MOTOR //
void drive(int speed){
    if(speed <= 0) {
        gpio_put(a1,false);
        gpio_put(a2,true);
    }
    else {
        gpio_put(a1,true);
        gpio_put(a2,false);
    }
    speed = abs(speed);
    pwm_set_gpio_level(pwma,speed);
    sleep_ms(1);
}

//  CONTROLLER //
float control(float kd, int desired_velocity, int velocity){
    float maxspeed = 5000.0;
    uint32_t amplification_factor = 1;          //      [degree/Volt]
    uint32_t paddleRadius = 1;                  //      [m]
    float velocity_error = velocity - desired_velocity;
    float control_signal = kd*(velocity_error);
    if (control_signal > maxspeed){
        control_signal = maxspeed;
    }
    if (control_signal < -1*maxspeed){
        control_signal = -1*maxspeed;
    }
    // control_signal = 0.0;
    int control_output = round(control_signal);
    return control_output;
}


// MAIN LOOP //
int main()
{
    //  INITIALIZE PADDLE
    init_sensor();                          //      "turn on" sensor
    init_driver();                          //      "turn on" driver
    stdio_init_all();                       //      "turn on" logic board
    
    //  Declare CONSTANTS
    int Kd = 55.0;                          //      Proportional control constant
    float desired_velocity = 10.0;        //     0 degrees + 60 units offset;
    int current_position;
    int last_position;
    int last_last_position;
    int current_velocity;
    int s_t;
    int e_t;
    int dt;
    int control_signal;
    int count;

	    //  START CONTROL LOOP
    float freqs[46] ={0.1,0.12,0.14,0.16,0.18,0.2,0.22,0.24,0.26,0.28,0.3,0.32,0.34,0.36,0.38,0.4,0.42,0.44,0.46,0.48,0.5,0.52,0.54,0.56,0.58,0.6,0.62,0.64,0.66,0.68,0.7,0.72,0.74,0.76,0.78,0.8,0.82,0.84,0.86,0.88,0.9,0.92,0.94,0.96,0.98,1};
    int index;
    while (1){
        count = count + 1;
        s_t = time_us_32();
        last_last_position = last_position;
        last_position = current_position;
        // sleep_ms(2);
        current_position = adc_read();
        e_t = time_us_32();
        dt = e_t - s_t;
        // current_velocity = getVelocity(current_position, last_position,dt);
        index = (int)round(count/2000) - 26843*0  +35;
        printf("\n %.2d ...", (int)index);
        printf("%.2f...", (float)current_position);
        // printf("%.2f...", (float)current_velocity);
        printf("%.2f...", (float)control_signal);
        printf("%.2f...", (float)s_t);

        // control_signal = 5000*sin((int)freqs[index]);
        control_signal = 100000*sin((float)freqs[index]*(3.1415/32*count));
        drive(control_signal);
    }
}

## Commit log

2022-05-25 cad update
    [91264A242_Alloy Steel Shoulder Screw.SLDPRT, 91781A113_18-8 Stainless Steel Slotted Flat Head Screw.SLDPRT, 9414T6_Set Screw Shaft Collar.SLDPRT, 98143A005_Nyl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]
2022-05-25 new CAD:
    [Base.SLDPRT]
2022-05-25 Adding LFS.
    [91264A242_Alloy Steel Shoulder Screw.SLDPRT, 91781A113_18-8 Stainless Steel Slotted Flat Head Screw.SLDPRT, 9414T6_Set Screw Shaft Collar.SLDPRT, 98143A005_Nyl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]
2022-05-25 Added Adafruit ROB14450 motor driver library.
2022-05-25 first print
    [Base.SLDPRT, Base.STL, HapticPaddle.SLDASM]
2022-05-26 Changed motor mount to be adjustable. Added AU logo in haptic.
    [Base.1.SLDPRT]
2022-05-26 sector pulley magnet slot
    [Drive_Wheel.SLDPRT, Hauptic_pcb.kicad_pcb, Hauptic_pcb.kicad_sch, Sector_Pulley.SLDPRT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]
2022-05-27 linearizing sensor output for control
2022-06-10 sensor linearization
2022-06-17 Working on integrating Seeeduino RP2040 with motor driver.
2022-06-17 motor test
2022-06-28 hardware updates
    [Base.SLDPRT, Drive_Wheel.SLDPRT, HapticPaddle.SLDASM, Hauptic_pcb.kicad_pcb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]
2022-06-30 cad updates:
    [Base.STL, HapticPaddle.SLDASM, Sector_Pulley_MRoffset.SLDPRT, Sector_Pulley_MRoffset.STL]
2022-11-15 printing update
    [2938T3_High-Load Oil-Embedded Sleeve Bearing-1.SLDPRT, 2938T3_High-Load Oil-Embedded Sleeve Bearing-1.STEP, 2938T3_High-Load Oil-Embedded Sleeve Bearing.SLDPRT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]
2024-01-19 Add files via upload
    added motor plate .stl
    [Motor_Plate.STL]
2026-01-07 Added Solidworks Hardware Files
    Solidworks Files for Haptic Symposium Version of the hAUptic Paddle
    [Front Calibration Support Plate.SLDPRT, Magnet Holder.SLDPRT, Mini Plate with Nut.SLDPRT, Motor_Pulley.SLDPRT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]
2026-01-07 Added Assembly and Clean Up
    Removed a temp file
    [HapKit Assembly.SLDASM]
2026-01-07 Added BOM
    [Parts to Order BOM.xlsx]
2026-01-08 Added Calibration Setup
    [Calibration Graph Setup.xlsx]
2026-01-08 Renamed Folder
    [Calibration Graph Setup.xlsx, Front Calibration Support Plate.SLDPRT, Front Calibration Support Plate.STEP, HapKit Assembly.SLDASM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]
2026-02-17 Update Parts to Order BOM.xlsx
    [Parts to Order BOM.xlsx]
